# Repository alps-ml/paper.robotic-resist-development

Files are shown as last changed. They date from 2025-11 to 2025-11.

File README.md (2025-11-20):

# ROS2 Workspace for MECA500 Robot Control for Nanofabrication

This repository contains the necessary tools and code to control a MECA500 robot 
developed in the [LINQS](https://linqs.stanford.edu/) lab, currently for nanofabrication tasks.
The project uses ROS2 Jazzy and provides an environment for both simulation and robot control through MoveIt.

At the moment we implement a resist development task. It identifies chiplets inside a chip-box, picks them up to move through developer and runs a nitrogen gun at the end controlled using a Serial-port controlled valve.

The hardware components that need to be 3D printed, can be found in `docs/assets/models`.

## Bill of Materials

| Component              | Description                                      | Product Number |
|------------------------|--------------------------------------------------|----------------|
| MECA500 Robot Arm      | Primary robotic arm for nanofabrication tasks    | Meca500        |
| End-effector - Gripper   | Mounts for Techni Tool Tweezer tips. Uses Dowel pins for alignment. | MEGP-25 LS        |
| Realsense   | Depth camera for object detection. | Realsense D405        |
| Tweezer Tips   | Techni-Pro Tweezer Tips. [Techni-Pro 758TW0304](https://www.techni-tool.com/category/Hand-And-Power-Tools/Hand-Tools/Tweezers/Replacement-Tip-Tweezers/758TW0304-758TW0304) | Techni-Pro 758TW0305      |
| Chip-box               | Holds chiplets for pickup and placing | Entegris H44-999-1415       |
| Nitrogen Valve           | Serial-port valve-controlled drying gun. |  [Beduan Solenoid Valve](https://www.amazon.com/Beduan-Normally-Closed-Electric-Solenoid/dp/B07N2LGFYS)   |
| Serial Relay       | USB Serial Port Relay Module. | [JESSINIE Relay Module](https://www.amazon.com/JESSINIE-Lightweight-Intelligent-Overcurrent-Protection/dp/B0BXDNNJ8K)    |
| Dowel Pins            | Used for angular alignment of tweezer tips. (M1.5 x 6mm)  | [Amazon Link](https://www.amazon.com/dp/B07ZF69XM1) |

## Setup Instructions

> [!IMPORTANT]  
> Please do not expect this project to just run for you. You can see it as inspiration, help with implementing some of the tasks. This is not a final library you can just install and run. 

The project also contains a few unfinished leads we were following, like recovering some old MoveIt controller or including an RRTC motion planning algorithm in moveit_linqs.

### Prerequisites
- Ubuntu 24.04
- [just](https://just.systems/) - A command runner (similar to make but simpler)

## Using the Workspace

All commands should be run from the root of the workspace directory. There's no need to modify your bashrc as the justfile handles environment sourcing.

### Running the Demo
The demo is simplest run by starting three different components and running these commands:

```bash
just meca-driver
just bringup
just meca-demo-develop 
```

### Available Commands

#### ROS2 Basic Commands
- **Run RViz2**:
  ```bash
  just rviz2
  ```

- **Run RViz2 with Meca Robot model**:
  ```bash
  just rviz2-meca
  ```

#### MoveIt Commands
- **Launch MoveIt with Meca Robot model**:
  ```bash
  just moveit-meca
  ```

#### General ROS2 Commands
- **Run any ROS2 command**:
  ```bash
  just ros2 <command>
  ```
  For example:
  ```bash
  just ros2 node list
  ```

### Installation

1. **Install ROS2 Jazzy**:
   ```bash
   just install-ros2-jazzy
   ```
   This will install:
   - ROS2 Jazzy desktop
   - Required development tools
   - Dependencies needed for the project

2. **Build the workspace**:
   ```bash
   just build_ws
   ```

3. **Update dependencies** (if needed):
   ```bash
   just rosdep_update
   ```

## Project Structure

The workspace is organized as follows:
- meca_controller: Controller nodes for the MECA500 robot
- meca_moveit_config: MoveIt configuration for motion planning
- mecademic_description: Robot description files (URDF, visualization)

## Running on Other Systems

If you need to run this on a non-Ubuntu system, you can use containerization:

### Using Toolbox on Other Linux Distributions

1. Install [toolbox](https://containertoolbx.org/)
2. Create an Ubuntu 24.04 container:
   ```bash
   toolbox create --distro ubuntu --release 24.04 ubuntu2404-ROS
   ```
3. Enter the toolbox:
   ```bash
   toolbox enter ubuntu2404-ROS
   ```
4. Inside the toolbox, clone this repository and follow the installation steps above

## Building

To rebuild the workspace after changes:
```bash
just build_ws
```

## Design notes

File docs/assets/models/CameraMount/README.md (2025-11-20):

Mounting Intel Realsense Camera D405
====================================
This mounts the RealSense Camera D405 on the last arm of the Mecademic M500 to view the tips of the tweezers.

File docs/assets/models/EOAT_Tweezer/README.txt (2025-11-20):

End of Arm Tooling
==================

This mounts the tweezer on a Mecademic Gripper MEGP 25LS.

The mount fits Techni Tool Tweezer [1] tips, but most of these tips are very similar.
To help on angular alignment, we use Dowel pins from Amazon (Dowel Pin, M1.5 x 6mm) e.g. these ones [2].

The tweezer tips are then only pressed into the 3d printed adapter.
They need to be printed twice and we print them with the screw recess towards the print plate.

[1] (https://www.techni-tool.com/category/Hand-And-Power-Tools/Hand-Tools/Tweezers/Replacement-Tip-Tweezers/758TW0304-758TW0304)
[2] https://www.amazon.com/dp/B07ZF69XM1

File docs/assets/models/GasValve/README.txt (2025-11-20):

Gascontrol
==========

We use the following valve to connect to our nitrogen lines.
 - Beduan 2 Way Normally Closed DC 12V Electric Solenoid Air Valve 1/4" NPT - https://www.amazon.com/Beduan-Normally-Closed-Electric-Solenoid/dp/B07N2LGFYS
 - USB Serial Port Relay Module - https://www.amazon.com/JESSINIE-Lightweight-Intelligent-Overcurrent-Protection/dp/B0BXDNNJ8K

The 3d printed mount allows to screw the valve on a Thorlabs post.

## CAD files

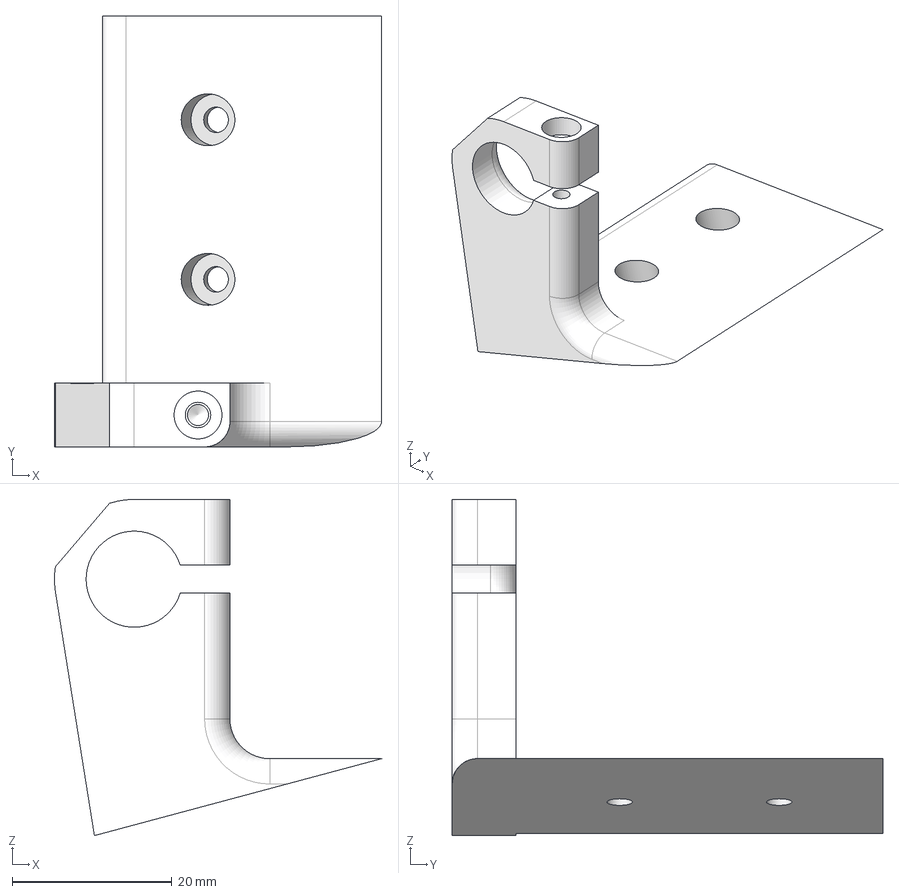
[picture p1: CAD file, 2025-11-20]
docs/assets/models/CameraMount/Camera Mount (angled) - Camera mount (top, side mount).step
41.0 x 54.0 x 42.1 mm

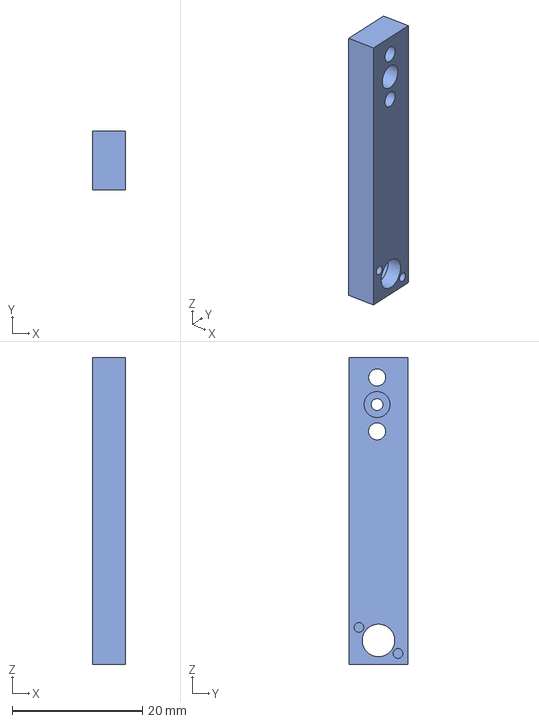
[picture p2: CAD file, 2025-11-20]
docs/assets/models/EOAT_Tweezer/Tweezer Upright (Long, 40mm) - Mount.step
5.00 x 9.00 x 47.2 mm

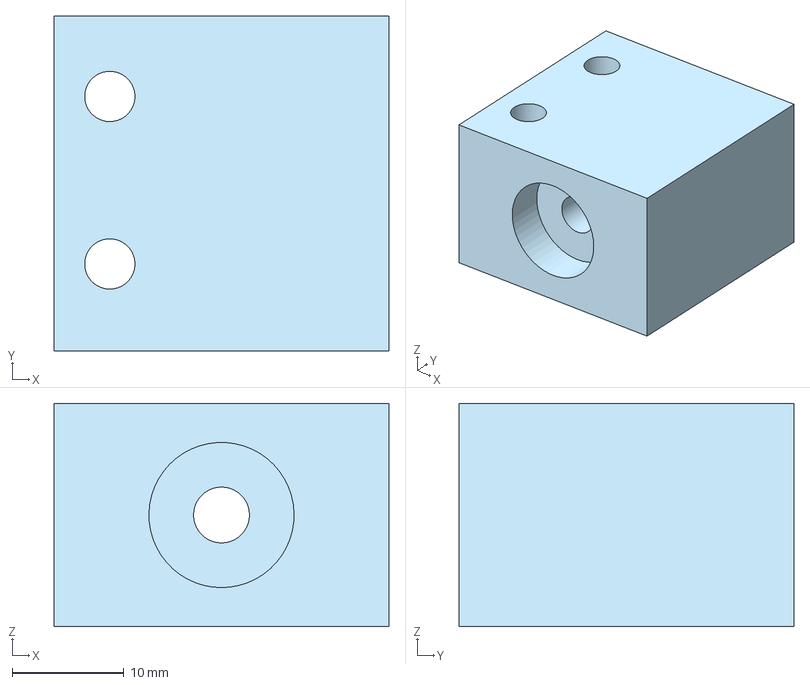
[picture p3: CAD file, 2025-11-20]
docs/assets/models/GasValve/GasValve.step
30.0 x 30.0 x 20.0 mm

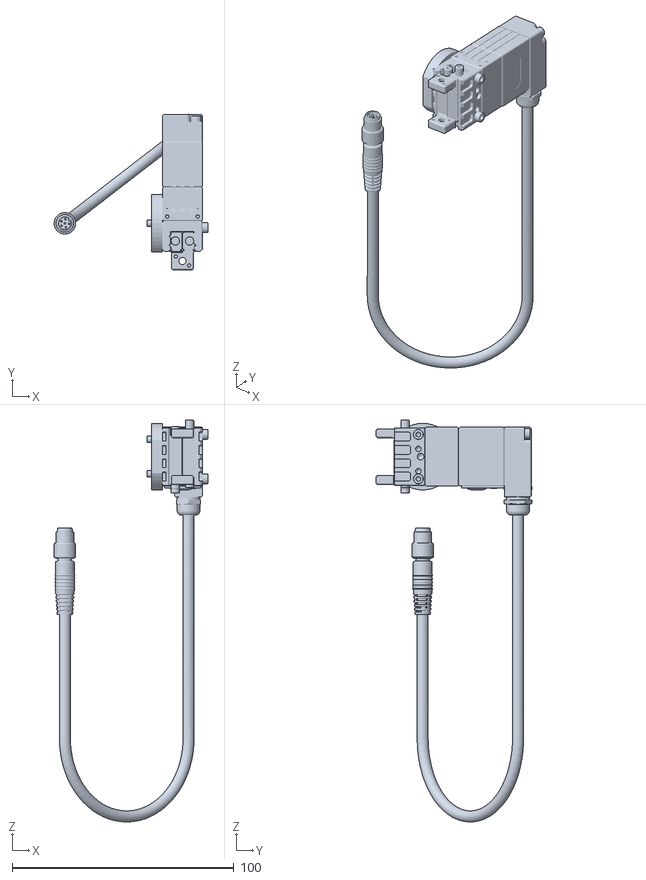
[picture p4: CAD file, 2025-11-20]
src/meca_moveit_config/meshes/Gripper_origin_moved_solidworks_stl.STL
69.3 x 70.1 x 181.1

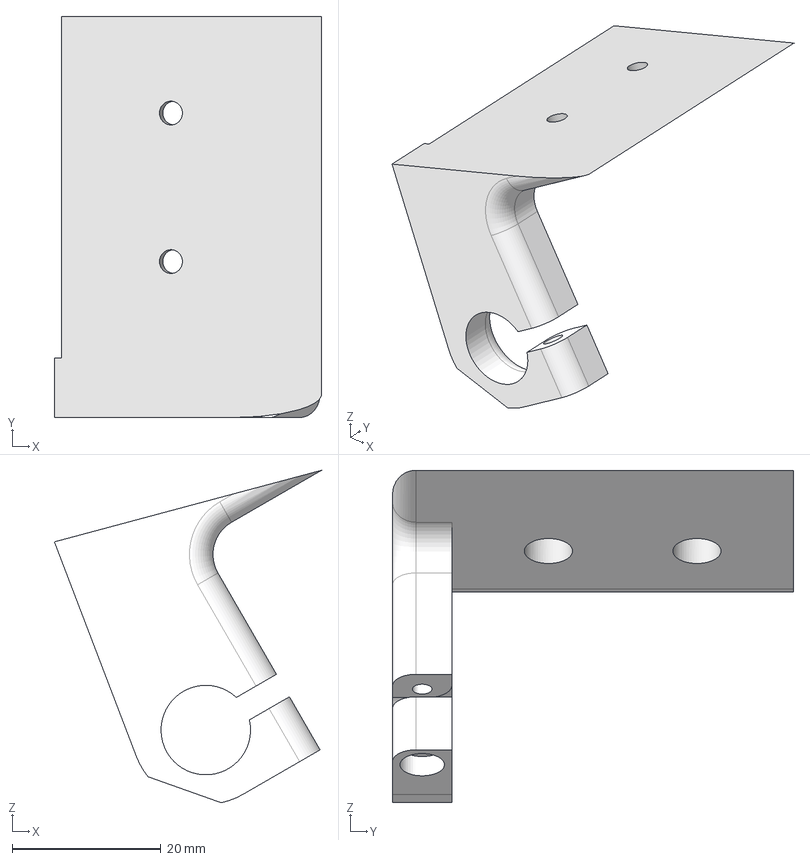
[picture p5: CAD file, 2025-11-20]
docs/assets/models/CameraMount/Camera Mount (angled) - Camera mount (bottom, side mount).step
36.0 x 54.0 x 44.8 mm

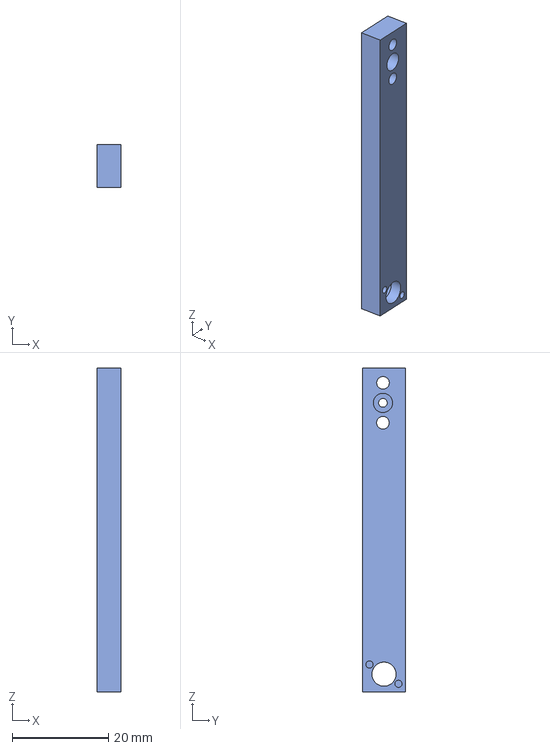
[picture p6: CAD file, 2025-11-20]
docs/assets/models/EOAT_Tweezer/Tweezer Upright (Long, 60mm) - Mount.step
5.00 x 9.00 x 67.2 mm

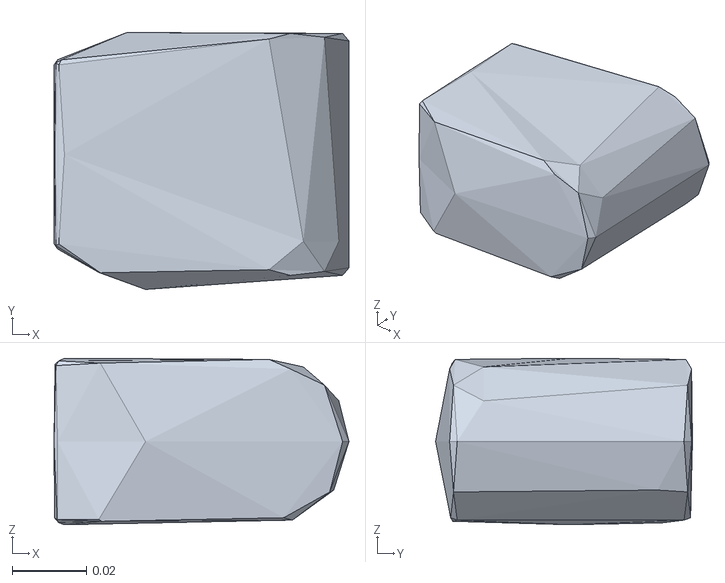
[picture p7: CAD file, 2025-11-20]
src/meca_moveit_config/meshes/meca_500_r3_j4_collision.stl
0.0797 x 0.0694 x 0.045

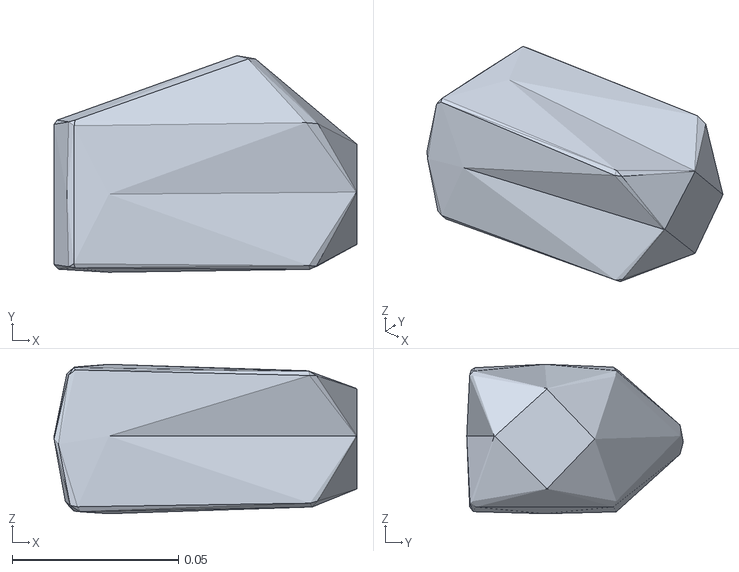
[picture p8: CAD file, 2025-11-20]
src/mecademic_description/meshes/meca_500_r3_j5_collision.stl
0.0912 x 0.0652 x 0.045

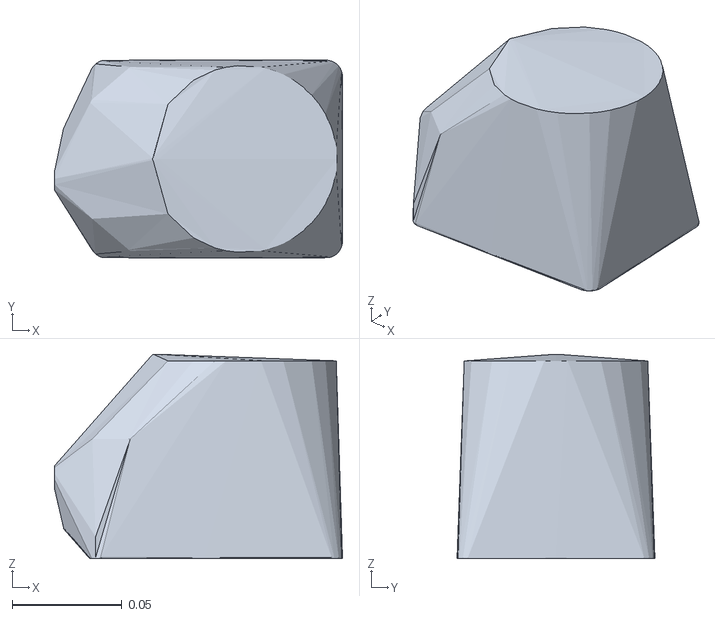
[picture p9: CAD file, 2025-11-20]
src/meca_moveit_config/meshes/meca_500_r3_base_collision.stl
0.131 x 0.09 x 0.093

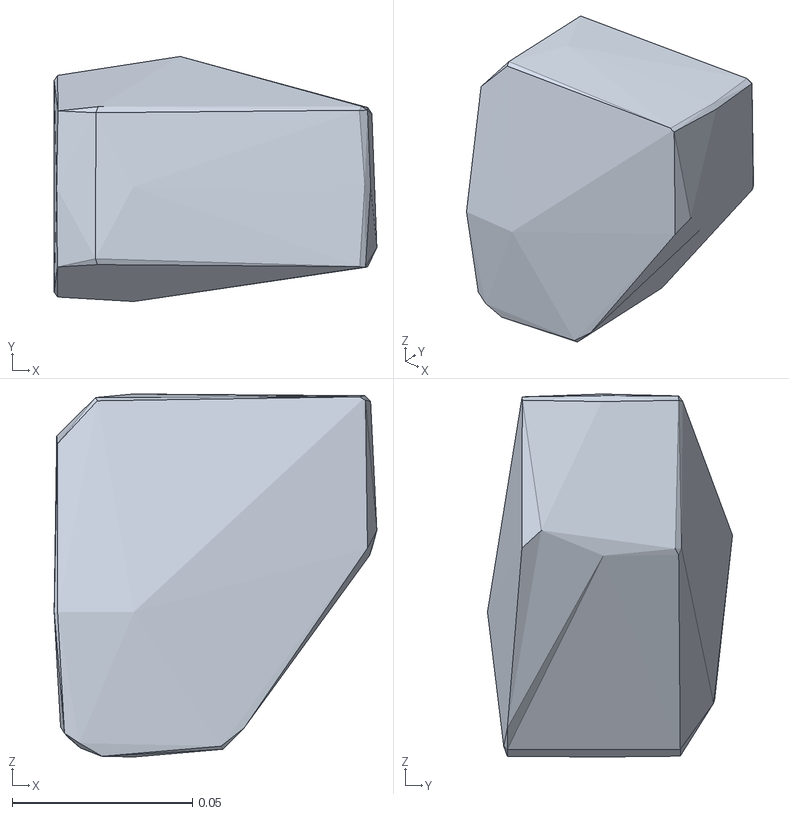
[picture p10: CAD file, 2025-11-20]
src/mecademic_description/meshes/meca_500_r3_j3_collision.stl
0.0896 x 0.068 x 0.101

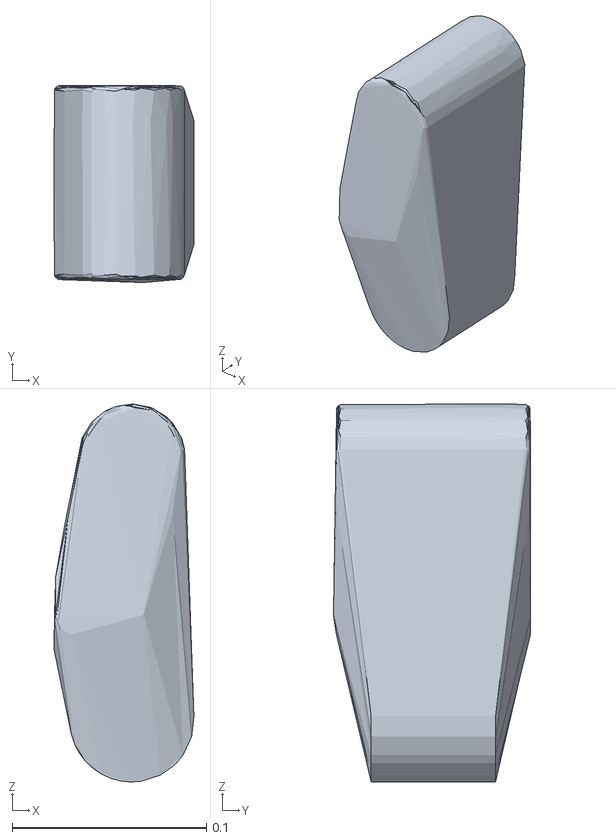
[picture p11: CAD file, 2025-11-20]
src/meca_moveit_config/meshes/meca_500_r3_j2_collision.stl
0.072 x 0.101 x 0.194

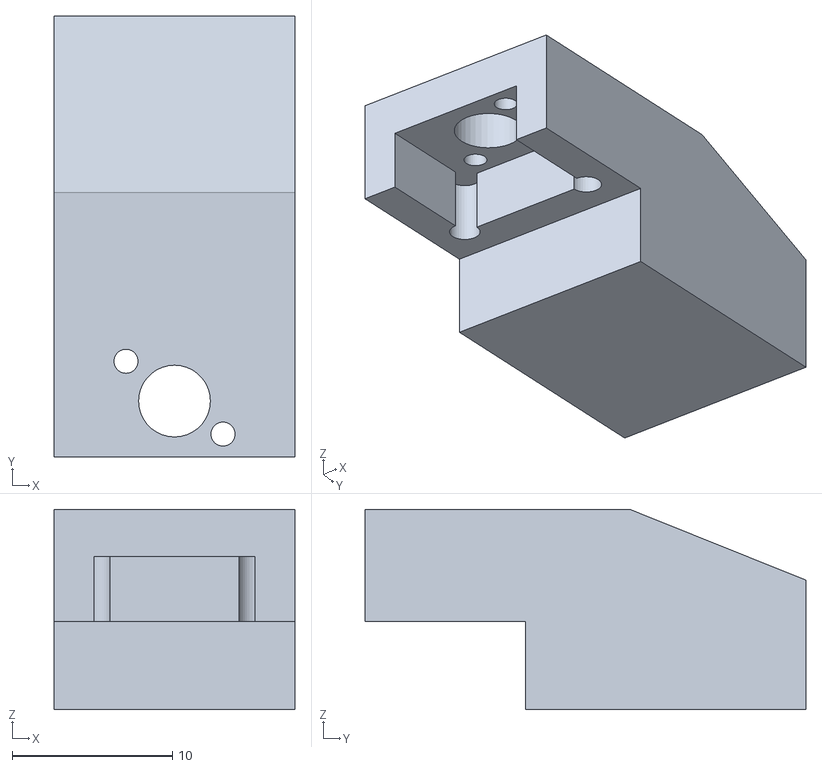
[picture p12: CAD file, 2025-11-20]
src/meca_moveit_config/meshes/Gripper_Finger_Origin_Centered_Nostep_5.5mm.STL
15.0 x 27.5 x 12.5

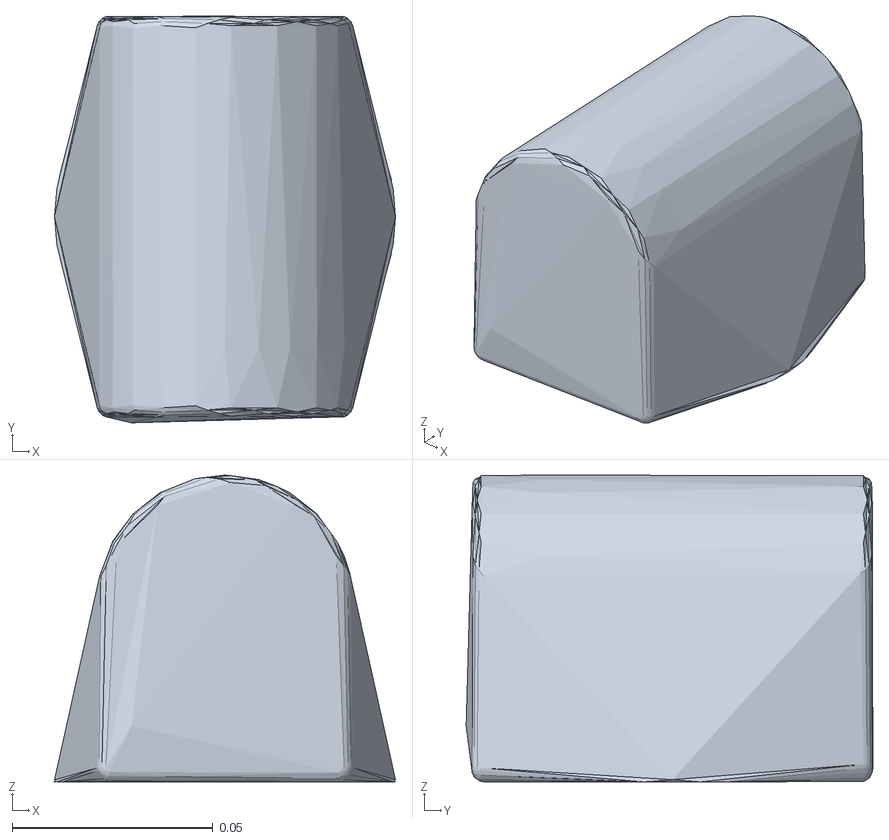
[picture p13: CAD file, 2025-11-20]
src/mecademic_description/meshes/meca_500_r3_j1_collision.stl
0.085 x 0.101 x 0.0765

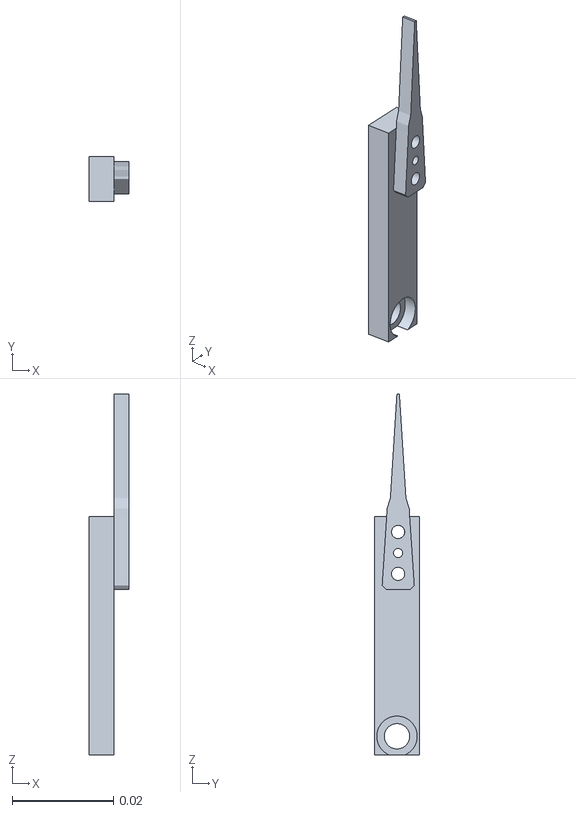
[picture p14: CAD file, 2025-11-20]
src/mecademic_description/meshes/Tweezer_finger_3mm.stl
0.008 x 0.009 x 0.0714

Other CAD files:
src/mecademic_description/meshes/Gripper_origin_moved.stl
src/meca_moveit_config/meshes/Gripper.stl
src/meca_moveit_config/meshes/Gripper_origin_moved.stl
src/meca_moveit_config/meshes/Tweezer_finger_1mm.stl
src/meca_moveit_config/meshes/beaker_hollow_tapered.stl
src/meca_moveit_config/meshes/beaker_test.stl
src/meca_moveit_config/meshes/cup_hollow_tapered.stl
src/meca_moveit_config/meshes/meca_500_r3_j6_collision.stl
src/mecademic_description/meshes/Gripper.stl
src/mecademic_description/meshes/Tweezer_finger.stl
src/mecademic_description/meshes/meca_500_r3_j6_collision.stl

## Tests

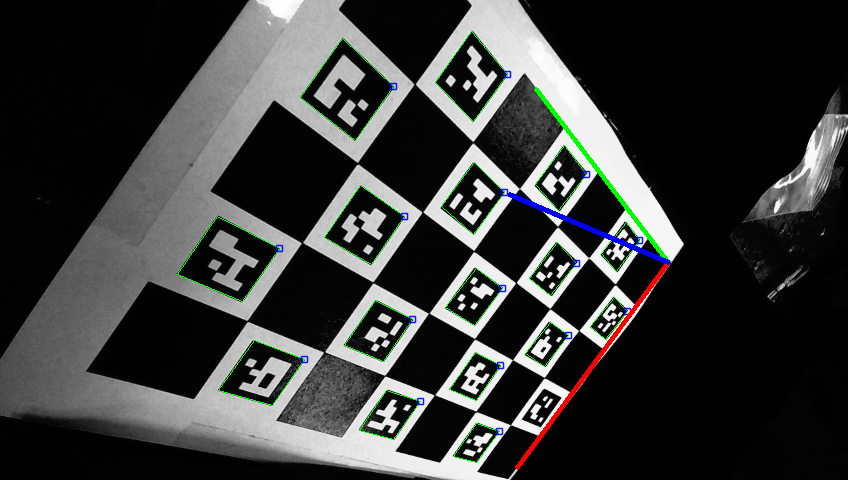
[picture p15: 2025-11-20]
src/meca_calibration/results_calibration/images_20250604/pose19.png

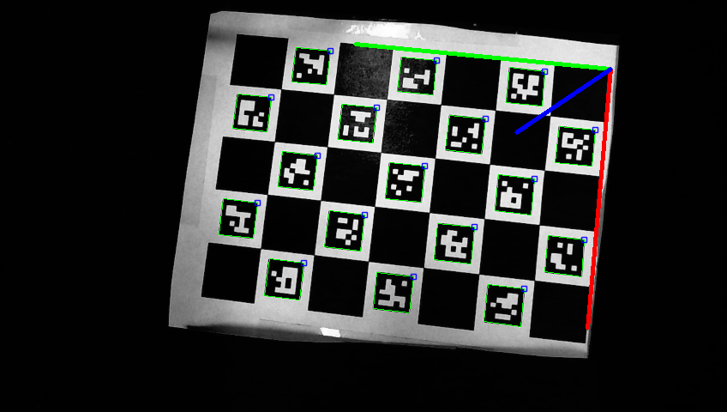
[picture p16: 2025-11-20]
src/meca_calibration/results_calibration/images_20250604/pose15.png

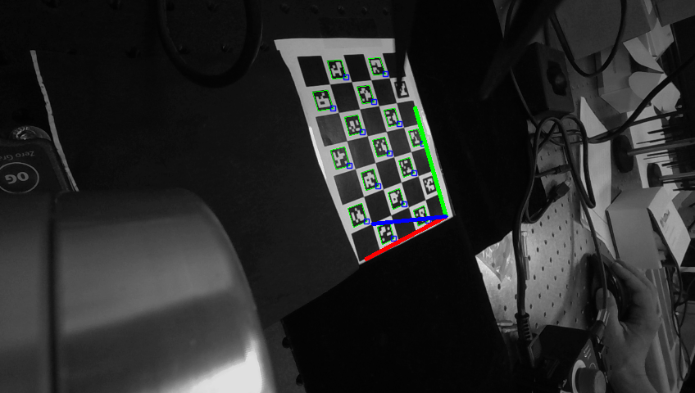
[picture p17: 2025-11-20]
src/meca_calibration/results_calibration/images_20250604/pose12.png

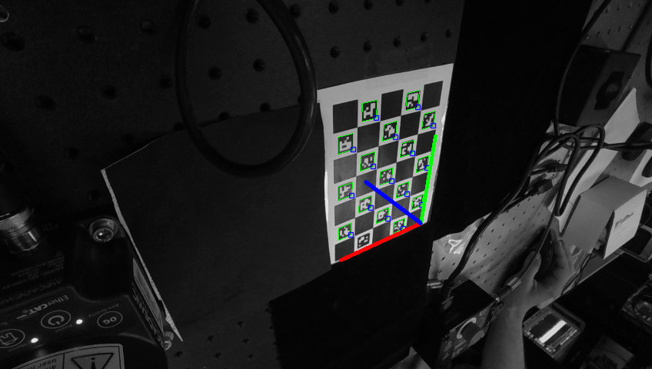
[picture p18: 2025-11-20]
src/meca_calibration/results_calibration/images_20250604/pose9.png

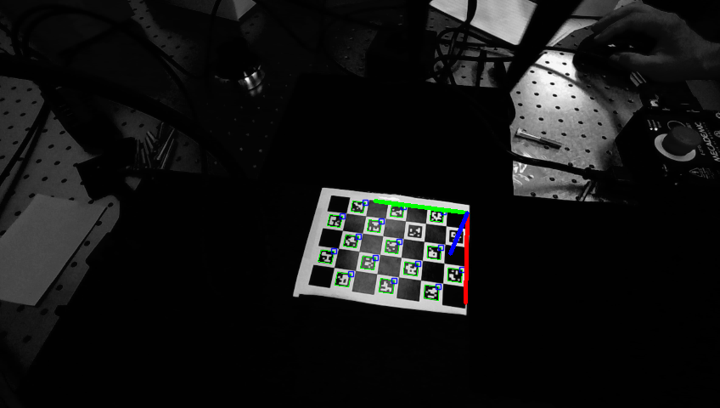
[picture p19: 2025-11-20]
src/meca_calibration/results_calibration/images_20250604/pose6.png

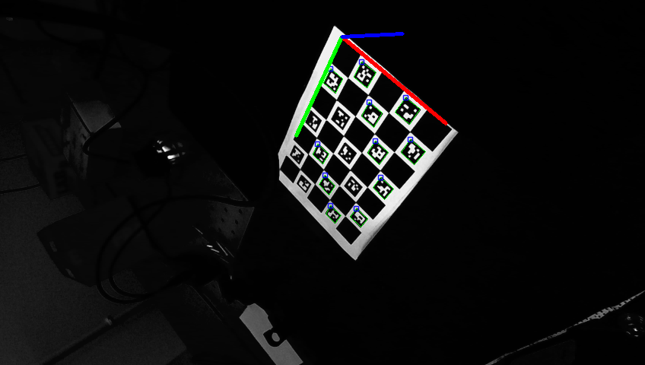
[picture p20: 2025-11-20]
src/meca_calibration/results_calibration/images_20250604/pose13.png

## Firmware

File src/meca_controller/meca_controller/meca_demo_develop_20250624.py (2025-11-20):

#!/usr/bin/env python3Publisher

'''
############################################################
############################################################
Purpose: This node, Meca_Control, was created to integrate/test motion planning
with the real robot by communicating over topics and with services. It
can be used to control both robots--hence it doesn't take a namespace.
Currently, "user" code can be written in the run() method to use this
ros2 system and move the robots. In the future, it would be great to
create a shell command prompt for the user to control the robots or get
info quickly without writing code; also, a way to create a separate script
that interacts with these control functions would be ideal so this file does
not get messy. But for now, this is the state of the codebase.

Date Created: 04/26/2022
Developers: Jessica Myers, [add name here]
University of Illinois Urbana-Champaign

############################################################
############################################################
'''

import math
import time
import traceback
import serial

import numpy as np

import rclpy # python library for ros2. needed for every ros2 node
from rclpy.node import Node
from rclpy.action import ActionClient
from rclpy.callback_groups import MutuallyExclusiveCallbackGroup, ReentrantCallbackGroup
from rclpy.qos import QoSProfile, ReliabilityPolicy, HistoryPolicy, DurabilityPolicy

import tf2_ros
import tf2_geometry_msgs
from scipy.spatial.transform import Rotation as R

from geometry_msgs.msg import Pose, PoseStamped, Quaternion, TransformStamped, Vector3, Twist, Accel
from sensor_msgs.msg import JointState
from std_srvs.srv import Trigger
from std_msgs.msg import Header
from builtin_interfaces.msg import Duration as RosDurationMsg

from moveit_msgs.action import MoveGroup
from moveit_msgs.msg import MotionPlanRequest, WorkspaceParameters, RobotState, Constraints, JointConstraint, PlanningOptions, PositionIKRequest
from moveit_msgs.srv import GetPositionIK 

from custom_interfaces.srv import GetMotionPlan, VisualizeMotionPlan, MoveJoints
from custom_interfaces.srv import GoToPose, MoveGripper, SetBlending, SetGripperForce, SetGripperVel, SetJointVel, SetJointAcc, MoveLin, MoveLinRelWrf, MovePoseEuler, WaitIdle, GetRtJointTorq, ClearMotion, Home
from custom_interfaces.msg import RobotStatus, GripperStatus
from custom_interfaces.msg import PoseStampedArray
from custom_interfaces.msg import CartesianTrajectory, CartesianTrajectoryPoint, CartesianPosture, CartesianTolerance
from custom_interfaces.action import FollowCartesianTrajectory

from meca_controller.meca_settings import ROBOT1 # ADJUST THESE GLOBAL CONSTANTS

# never use scientific notation, always 3 digits after the decimal point
np.set_printoptions(suppress=True, precision=3) 

class Meca_Control(Node):
    def __init__(self):
        super().__init__("meca_control")

        self._robot1_ns = ROBOT1['namespace']
        self._move_speed = ROBOT1['move_speed']

        # Subscribe to keep up to date on current joint angles, pose, and status of the robot (may not need all these):
        # We always just want the latest information.
        self.joint_subscriber_robot1_ = self.create_subscription(JointState, "/joint_states",
                                                                 self.update_robot1_joints_callback, 1)
        self.pose_subscriber_robot1_ = self.create_subscription(Pose, f"{self._robot1_ns}/pose",
                                                                 self.update_robot1_pose_callback, 1)
        self.gripper_subscriber_robot1_ = self.create_subscription(GripperStatus, f"{self._robot1_ns}/gripper_status",
                                                                 self.update_robot1_gripper_status_callback, 1)
        self.status_subscriber_robot1_ = self.create_subscription(RobotStatus, f"{self._robot1_ns}/robot_status",
                                                                 self.update_robot1_status_callback, 1)

        # Initialize variables that will be set later:
        self.current_joints_robot1 = None
        self.current_pose_robot1 = None
        self.current_gripper_status_robot1 = None
        self.current_robot1_status = None

        # Define the QoS profile for sensor data (latest data only)
        qos_profile_sensor_data = QoSProfile(
            reliability=ReliabilityPolicy.RELIABLE,
            history=HistoryPolicy.KEEP_LAST,
            depth=1,
            durability=DurabilityPolicy.VOLATILE
        )

        self.chip_poses_subscriber_ = self.create_subscription(
            PoseStampedArray,
            '/chip_pose_calculator/detected_chip_world_poses',
            self.chip_poses_callback,
            qos_profile=qos_profile_sensor_data)  # Use explicit QoS profile
        self.latest_chip_poses_ = [] # List to store all received chip poses
        self.get_logger().info("Subscribed to /chip_pose_calculator/detected_chip_world_poses with sensor QoS")
        
        # Add refresh detection service client
        self.refresh_detection_client = self.create_client(
            Trigger, 
            '/chip_pose_calculator/refresh_detection'
        )
        self.get_logger().info("Created refresh detection service client")
        
        # Add debugging for topic connection
        self.get_logger().info("=== TOPIC SUBSCRIPTION DEBUG ===")
        self.get_logger().info(f"Topic: /chip_pose_calculator/detected_chip_world_poses")
        self.get_logger().info(f"QoS Profile: RELIABLE, KEEP_LAST, DEPTH=1, VOLATILE")
        self.get_logger().info(f"Message type: PoseStampedArray")
        self.get_logger().info("=== END SUBSCRIPTION DEBUG ===")
        
        # Add MoveIt2 interface
        self._moveit_callback_group = ReentrantCallbackGroup()
        
        # Action client for MoveIt2
        self.moveit_action_client = ActionClient(
            self,
            MoveGroup,
            'move_action',
            callback_group=self._moveit_callback_group
        )
        
        # Wait for MoveIt to be available
        if not self.moveit_action_client.wait_for_server(timeout_sec=2.0):
            self.get_logger().warn('MoveIt action server not available, proceeding without it.')
            self.moveit_available = False
        else:
            self.get_logger().info('MoveIt action server found and ready.')
            self.moveit_available = True

        self._cart_traj_action_client = ActionClient(self, 
                                                     FollowCartesianTrajectory, 
                                                     f'{self._robot1_ns}/meca_arm_controller/follow_cartesian_trajectory')
       
        # Wait for Cartesian Trajectory to be available
        if not self._cart_traj_action_client.wait_for_server(timeout_sec=2.0):
            self.get_logger().error('Cartesian Trajectory action server not available. Needed for some pathplanning.')
            raise Exception('Cartesian Trajectory action server not available. Needed for some pathplanning.')

        # TF buffer for coordinate transformations
        self.tf_buffer = tf2_ros.Buffer()
        self.tf_listener = tf2_ros.TransformListener(self.tf_buffer, self)

        # Add IK Service Client
        self.ik_client = self.create_client(GetPositionIK, '/compute_ik')
        
        self.meca_arm_joint_names = [
            "meca_axis_1_joint", "meca_axis_2_joint", "meca_axis_3_joint",
            "meca_axis_4_joint", "meca_axis_5_joint", "meca_axis_6_joint"
        ]

        self.wait_idle_client = self.create_client(WaitIdle, f"{self._robot1_ns}/wait_idle")
        self.clear_motion_client = self.create_client(ClearMotion, f"{self._robot1_ns}/clear_motion")
        self.home_client = self.create_client(Home, f"{self._robot1_ns}/home")

        self.move_pose_client = self.create_client(MovePoseEuler, f'{self._robot1_ns}/move_pose') 

        # --- Simplified Chip Detection ---
        # The detection node now provides stable poses, so we just store them directly
        self.latest_chip_poses_ = []  # List to store stable chip poses
        
        # --- Z Height Measurement Storage ---
        self.measured_grasp_z_height_ = None  # Store measured Z height for reuse
        
        # --- Gripper Configuration ---
        self.GRIPPER_OPEN_POS_MM = 18.0      # Gripper position when fully open
        self.GRIPPER_CLOSED_POS_MM = 9.5     # Gripper position when closed on chip
        self.GRIPPER_PLACE_POS_MM = 14.0     # Gripper position when placing chip (partially open)

        # --- Message Tracking ---
        self.message_counter = 0
        self.last_message_time = None

    def wait_for_initialization(self, timeout_length=2):
        """
        Purpose: Parts of this code rely upon getting information from topics published to by the meca_driver, such as current_joints.
                Errors will occur if the main code is executed before these are assigned (e.g. motion plan but not yet received the
                current joint states from the subscriber). This function will wait until the critical variables are set so that all
                the code runs as intended.

                -timeout_length: amount of time in seconds that should wait to receive data from both robots before beginning code execution;
                            after timeout period, just waits for data from one robot to begin because assumes you are only using 1 robot.

                TODO add to the critical init variables as code is built.
        """
        time_start = time.time()
        print('waiting to receive meca state data...')
        
        while rclpy.ok():
            rclpy.spin_once(self) # spin once while we wait to avoid blocking any callbacks. (like the data we are waiting on)
            if (self.current_joints_robot1 is not None):
                print('...received data for robot, starting now.')
                return

            # If timeout period has elapsed, only check for data being received from one robot before starting:
            if ((time.time() - time_start) >= timeout_length) and (self.current_joints_robot1 is not None):
                print('...received data for at least one robot, starting now because timeout has occurred waiting.\n')
                return

    def run(self):
        """
        Purpose: A space to write user code to control the robots. Example commands given here.
        
        TODO in the future, create a better way for the user to add code that doesn't involve editing this file.
        Currently unsure how to do this.

        NOTE: Everything involving the ros2 collision detection / urdf / visualization / motion planning has joint
        angles in RADIANS. The mecademicpy interface uses DEGREES for the MoveJoints command.
        """
        # Safety config
        self.set_joint_vel(self._robot1_ns, self._move_speed)
        self.set_gripper_force(self._robot1_ns, 5)
        self.move_gripper(self._robot1_ns, position=self.GRIPPER_OPEN_POS_MM)

        self.move_joints(np.array([0, 0, 0, 0, 0, 0]), self._robot1_ns)
        self.home(self._robot1_ns)
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

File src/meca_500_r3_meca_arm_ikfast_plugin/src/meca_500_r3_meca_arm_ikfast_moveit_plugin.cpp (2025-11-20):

/*********************************************************************
 *
 * Software License Agreement (BSD License)
 *
 * Copyright (c) 2013, Dave Coleman, CU Boulder; Jeremy Zoss, SwRI; David Butterworth, KAIST; Mathias Lüdtke, Fraunhofer
 *IPA
 * All rights reserved.
 *
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
 *     * Redistributions of source code must retain the above copyright
 *       notice, this list of conditions and the following disclaimer.
 *     * Redistributions in binary form must reproduce the above copyright
 *       notice, this list of conditions and the following disclaimer in the
 *       documentation and/or other materials provided with the distribution.
 *     * Neither the name of the all of the author's companies nor the names of its
 *       contributors may be used to endorse or promote products derived from
 *       this software without specific prior written permission.
 *
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
 *********************************************************************/

/*
 * IKFast Kinematics Solver Plugin for MoveIt wrapping an ikfast solver from OpenRAVE.
 *
 * AUTO-GENERATED by create_ikfast_moveit_plugin.py in moveit_kinematics package.
 *
 * This file, including the ikfast cpp from OpenRAVE below, forms a MoveIt kinematics plugin.
 */

#include <rclcpp/rclcpp.hpp>
#include <moveit/kinematics_base/kinematics_base.hpp>
#include <moveit/robot_state/robot_state.hpp>
#include <Eigen/Geometry>
#include <tf2_kdl/tf2_kdl.hpp>
#include <tf2_eigen/tf2_eigen.hpp>
#include <moveit/utils/logger.hpp>
#include <meca_500_r3_meca_arm_ikfast_plugin/ikfast_kinematics_parameters.hpp>

using namespace moveit::core;

// Need a floating point tolerance when checking joint limits, in case the joint starts at limit
const double LIMIT_TOLERANCE = .0000001;
/// \brief Search modes for searchPositionIK(), see there
enum SEARCH_MODE
{
  OPTIMIZE_FREE_JOINT = 1,
  OPTIMIZE_MAX_JOINT = 2
};

namespace meca_500_r3_meca_arm
{
namespace
{
rclcpp::Logger getLogger()
{
  return moveit::getLogger("moveit.core.meca_500_r3_meca_arm_ikfast_solver");
}
}  // namespace

#define IKFAST_NO_MAIN  // Don't include main() from IKFast

/// \brief The types of inverse kinematics parameterizations supported.
///
/// The minimum degree of freedoms required is set in the upper 4 bits of each type.
/// The number of values used to represent the parameterization ( >= dof ) is the next 4 bits.
/// The lower bits contain a unique id of the type.
enum IkParameterizationType
{
  IKP_None = 0,
  IKP_Transform6D = 0x67000001,    ///< end effector reaches desired 6D transformation
  IKP_Rotation3D = 0x34000002,     ///< end effector reaches desired 3D rotation
  IKP_Translation3D = 0x33000003,  ///< end effector origin reaches desired 3D translation
  IKP_Direction3D = 0x23000004,    ///< direction on end effector coordinate system reaches desired direction
  IKP_Ray4D = 0x46000005,          ///< ray on end effector coordinate system reaches desired global ray
  IKP_Lookat3D = 0x23000006,       ///< direction on end effector coordinate system points to desired 3D position
  IKP_TranslationDirection5D = 0x56000007,  ///< end effector origin and direction reaches desired 3D translation and
  /// direction. Can be thought of as Ray IK where the origin of the ray must
  /// coincide.
  IKP_TranslationXY2D = 0x22000008,             ///< 2D translation along XY plane
  IKP_TranslationXYOrientation3D = 0x33000009,  ///< 2D translation along XY plane and 1D rotation around Z axis. The
  /// offset of the rotation is measured starting at +X, so at +X is it 0,
  /// at +Y it is pi/2.
  IKP_TranslationLocalGlobal6D = 0x3600000a,  ///< local point on end effector origin reaches desired 3D global point
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

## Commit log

2025-11-20 Code for paper release.
    [Camera Mount (angled) - Camera mount (bottom, side mount).step, Camera Mount (angled) - Camera mount (top, side mount).step, GasValve.step, Gripper.stl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]
2025-11-20 docs folder name changed
    [Camera Mount (angled) - Camera mount (bottom, side mount).step, Camera Mount (angled) - Camera mount (top, side mount).step, GasValve.step, Tweezer Upright (Lo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]
2025-11-20 chore: deleted files where not committed.
    [Camera Mount (angled) - Camera mount (bottom, side mount).step, Camera Mount (angled) - Camera mount (top, side mount).step, GasValve.step, Tweezer Upright (Lo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]
